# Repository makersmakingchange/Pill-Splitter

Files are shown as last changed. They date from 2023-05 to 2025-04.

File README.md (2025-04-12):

# Pill Splitter
The pill slicer is an easy to use device that slices a pill into two. This device is intended for users that need to cut pills into two and have difficulty doing so without crushing the pill.

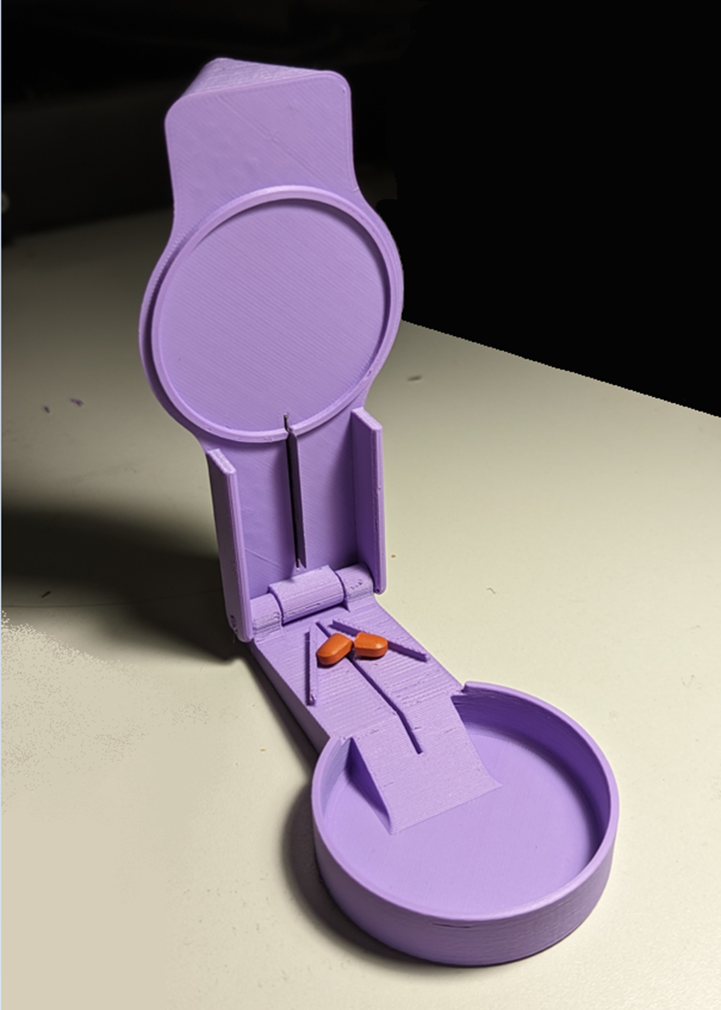
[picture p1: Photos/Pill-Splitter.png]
Picture of Pill Splitter.


## Makers Making Change Assistive Device Library
 - https://www.makersmakingchange.com/s/product/pill-splitter/01tJR00000092fJYAQ

## How to Obtain a Pill Splitter
### 1. Do it Yourself (DIY) or Do it Together (DIT)

This is an open-source assistive technology, so anyone is free to build it. All of the files and instructions required to build the Pill Splitter are contained within this repository. Refer to the Maker Checklist below.

### 2. Request a build of this device

If you would like to obtain a Pill Splitter, you may submit a build request through the [MMC Library Page](https://makersmakingchange.com/project/pill-splitter/). The requestor is responsible for the cost of materials and any shipping.

### 3. How to build this device for someone else

If you have the skills and equipment to build this device, and would like to donate your time to create the switch for someone who needs it, visit the [MMC Maker Wanted](https://makersmakingchange.com/maker-wanted/) section.

## Getting Started

### 1. Read the Makers Checklist

[The Makers Checklist](/Documentation/Pill_Splitter_Maker_Checklist_V1.0.pdf)

### 2. Order the Off-The-Shelf Components

The [Bill of Materials](/Documentation/Pill_Splitter_BOM_V1.0.xlsx) lists all of the parts and components required to build the Pill Splitter. The razor blades are also online or may be available in smaller quantities at your local dollar store.

### 3. Print the 3D Printable components

Print the components

All of the files and individual print files can be in the [/Build_Files/3D_Printing_Files](/Build_Files/3D_Printing_Files/) folder.

### 4. Assemble the Pill Splitter

Reference the [Assembly Guide](/Documentation/Pill_Splitter_Assembly_Guide_V1.0.pdf) for the tools and steps required to build each portion.

## Files
### Documentation
| Document             | Version | Link |
|----------------------|---------|------|
| Design Rationale     | 1.0     | [Pill_Splitter_Design_Rationale](/Documentation/Pill_Splitter_Design_Rationale_V1.0.pdf)     |
| Maker Checklist      | 1.0     | [Pill_Splitter_Maker_Checklist](/Documentation/Pill_Splitter_Maker_Checklist_V1.0.pdf)     |
| Bill of Materials    | 1.0     | [Pill_Splitter_Bill_of_Materials](/Documentation/Pill_Splitter_BOM_V1.0.xlsx)     |
| 3D Printing Guide    | 1.0     | [Pill_Splitter_3D_Printing_Guide](/Documentation/Pill_Splitter_3D_Printing_Guide_V1.0.pdf)     |
| Assembly Guide       | 1.0     | [Pill_Splitter_Assembly_Guide](/Documentation/Pill_Splitter_Assembly_Guide_V1.0.pdf)     |
| User Guide           | 1.0     | [Pill_Splitter_User_Guide](/Documentation/Pill_Splitter_User_Guide_V1.0.pdf)    |
| Changelog            | 1.0     | [Pill_Splitter_Changelog](/Documentation/Pill_Splitter_Changelog_V1.0.pdf)     |

### Design Files
 - [CAD Files](/Design_Files)

### Build Files
 - [3D Printing Files](/Build_Files/3D_Printing_Files)

## Attribution

Designers:
 - Initial design by [Aliaksei Petsiuk @apetsiuk - MyMiniFactory](https://www.myminifactory.com/users/apetsiuk)
 - Modifications and documentation by Neil Squire Society/Makers Making Change

## License
Everything needed or used to design, make, test, or prepare the Pill Splitter is licensed under the [Attribution-NonCommercial-ShareAlike 4.0 ](https://creativecommons.org/licenses/by-nc-sa/4.0/).

Accompanying material such as instruction manuals, videos, and other copyrightable works that are useful but not necessary to design, make, test, or prepare the Pill Splitter are published under a Creative Commons Attribution-ShareAlike 4.0 license https://creativecommons.org/licenses/by-sa/4.0/ (CC BY-SA 4.0).

---

<!-- ABOUT MMC START -->
## About Makers Making Change
[Makers Making Change Logo](https://www.makersmakingchange.com/)

Makers Making Change is a program of [Neil Squire](https://www.neilsquire.ca/), a Canadian non-profit that uses technology, knowledge, and passion to empower people with disabilities.

Makers Making Change leverages the capacity of community based Makers, Disability Professionals and Volunteers to develop and deliver affordable Open Source Assistive Technologies.

 - Website: [www.MakersMakingChange.com](https://www.makersmakingchange.com/)
 - GitHub: [makersmakingchange](https://github.com/makersmakingchange)
 - Bluesky: [@makersmakingchange.bsky.social](https://bsky.app/profile/makersmakingchange.bsky.social)
 - Instagram: [@makersmakingchange](https://www.instagram.com/makersmakingchange)
 - Facebook: [makersmakechange](https://www.facebook.com/makersmakechange)
 - LinkedIn: [Neil Squire Society](https://www.linkedin.com/company/neil-squire-society/)
 - Thingiverse: [makersmakingchange](https://www.thingiverse.com/makersmakingchange/about)
 - Printables: [MakersMakingChange](https://www.printables.com/@MakersMakingChange)

### Contact Us
For technical questions, to get involved, or to share your experience we encourage you to [visit our website](https://www.makersmakingchange.com/) or [contact us](https://www.makersmakingchange.com/s/contact).
<!-- ABOUT MMC END -->

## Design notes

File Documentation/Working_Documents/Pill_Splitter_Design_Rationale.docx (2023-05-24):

# Introduction

The pill slicer is an easy to use device that slices a pill into two. This device is intended for users that need to cut pills into two and have difficulty doing so without crushing the pill.

# Research

Name | Image | Price | Link

Commercial

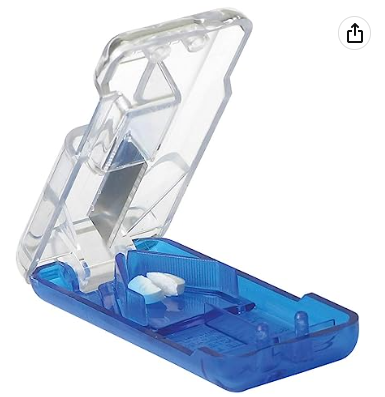
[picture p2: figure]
Image of the EZY DOSE Pill Cutter

EZY DOSE Pill Cutter | | 12.25 | Link (https://www.amazon.ca/Ezy-Dose-Pill-Cutter-Dispenser/dp/B001KYVO78?hvadid=459657913388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)

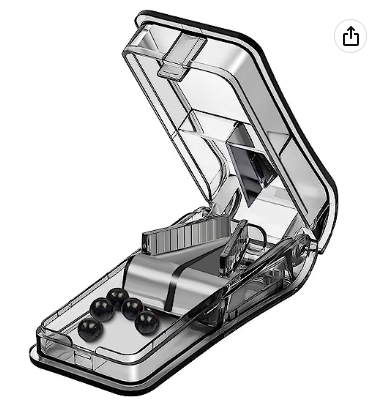
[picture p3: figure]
Image of the Pill Cutter

Pill Cutter | | 8.99 | Link (https://www.amazon.ca/Pill-Splitters-Portable-Vitamins-Medication/dp/B09TZSBPQC?s=hpc)

DIY

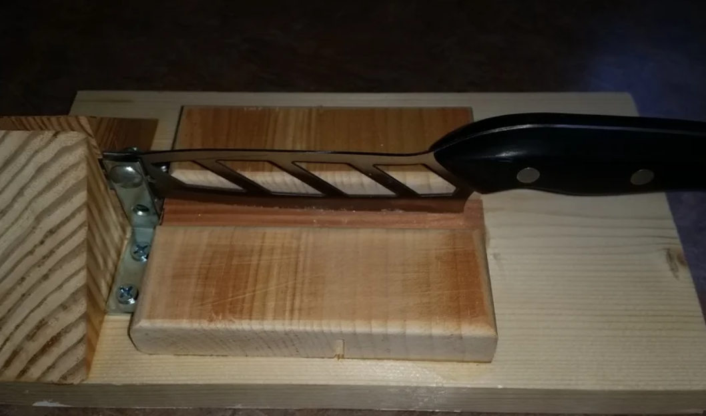
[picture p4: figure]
A knife bolted to a metal bracket on several pieces of wood.

DIY Multiple Pill Splitter | | N/A | Link (https://www.instructables.com/DIY-Multiple-Pill-Splitter/)

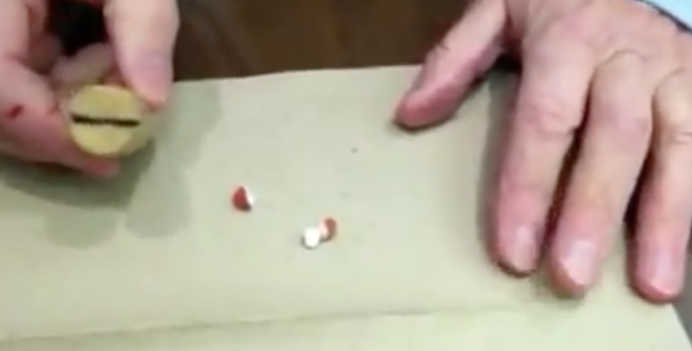
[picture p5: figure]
A crushed pill on a cutting board between two hands. One hand is holding a homemade pill splitter.

Homemade Pill Splitter | | N/A | Link (https://www.wpr.org/homemade-pill-splitter)

# Requirements

## Goals

G01 | Device must be able to easily slice a pill

## Functional Requirements

F01 | Device must use a replaceable slicing device
F02 | Device must be safe and difficult to injure yourself with.

## Constraints

C01 | Design must be entirely 3D printed

# Conceptual Design

Initial design was found on myminifactory.com by user Aliaksei Petsiuk @apetsiuk - MyMiniFactory (https://www.myminifactory.com/users/apetsiuk)

# Prototyping

After inspecting the files for the first version, it was found that there was no blade or method of slicing the pill mentioned in the original device posting. A version was designed that uses a standard disposable safety razor blade.

# Testing

After the first print of the updated design, it was found that the overhangs were too steep for most printers, leading to poor surface quality.

# Detailed Design

A final version was designed with better overhangs that are more printable and reduced print time by an hour.

# Opportunities for Improvement

More safety features could be added in addition to the blade fence to improve the safety of the device.

© 2023 by Neil Squire. This work is licensed under the CC BY SA 4.0 License: http://creativecommons.org/licenses/by-sa/4.0 Files available at https://makersmakingchange.com/project/pill-slicer/ Page 1 of 1

V1.0 | March 2023 Pill Slicer Design Rationale

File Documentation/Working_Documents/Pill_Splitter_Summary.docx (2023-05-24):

# Title

Pill Slicer

## Subtitle

The pill slicer is an easy to use device that slices a pill into two.

## Device Details

### Overview

This device is intended for users that need to cut pills into two and have difficulty doing so without crushing the pill.

### Usage

To use, place a pill over the slot on the lower base, and center it between the two fences. Close the upper half of the device, and the built in razor blade will slice the pill in half.

### Cost

<$5

### Build Instructions

After assembling the device as in the assemble guide, the razor blade can be flipped or replaced if the blade dulls and no longer cuts properly.

#### Skills Required

- 3D printing

#### Time Required

3D printing time: 394 min (6h34min)

Assembly Time: 5 min

#### Tools

- 3D printer
- Pliers
- Hobby knife
- Sandpaper

#### Components

#### 3D Printing

- Upper
- Lower
- Hinge Pin
- Blade Pin

### Attribution

Initial design by Aliaksei Petsiuk @apetsiuk - MyMiniFactory (https://www.myminifactory.com/users/apetsiuk)

Modifications and documentation by Neil Squire Society/Makers Making Change

© 2023 by Neil Squire. This work is licensed under the CC BY SA 4.0 License: http://creativecommons.org/licenses/by-sa/4.0 Files available at https://makersmakingchange.com/project/pill-slicer/ Page 1 of 1

V1.0 | March 2023 Pill Slicer Summary

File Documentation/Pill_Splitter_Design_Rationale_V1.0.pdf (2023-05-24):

V1.0 | March 2023

## Pill Slicer

## DESIGN RATIONALE

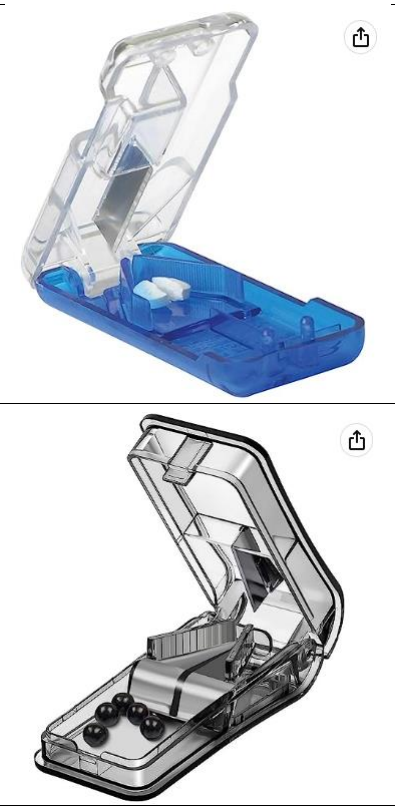
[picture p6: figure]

© 2023 by Neil Squire. (https://neilsquire.ca/)
This work is licensed under the CC BY SA 4.0 License: http://creativecommons.org/licenses/by-sa/4.0
Files available at https://makersmakingchange.com/project/pill-slicer/ | Page 1 of 3

### Introduction

The pill slicer is an easy to use device that slices a pill into two. This device is intended for users that need to cut pills into two and have difficulty doing so without crushing the pill.

### Research

Name | Image | Price | Link
Commercial
EZY DOSE Pill Cutter | 12.25 | Link (https://www.amazon.ca/Ezy-Dose-Pill-Cutter-Dispenser/dp/B001KYVO78?hvadid=459657913388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)
Pill Cutter | 8.99 | Link (https://www.amazon.ca/Pill-Splitters-Portable-Vitamins-Medication/dp/B09TZSBPQC?s=hpc)

DIY

## DESIGN RATIONALE

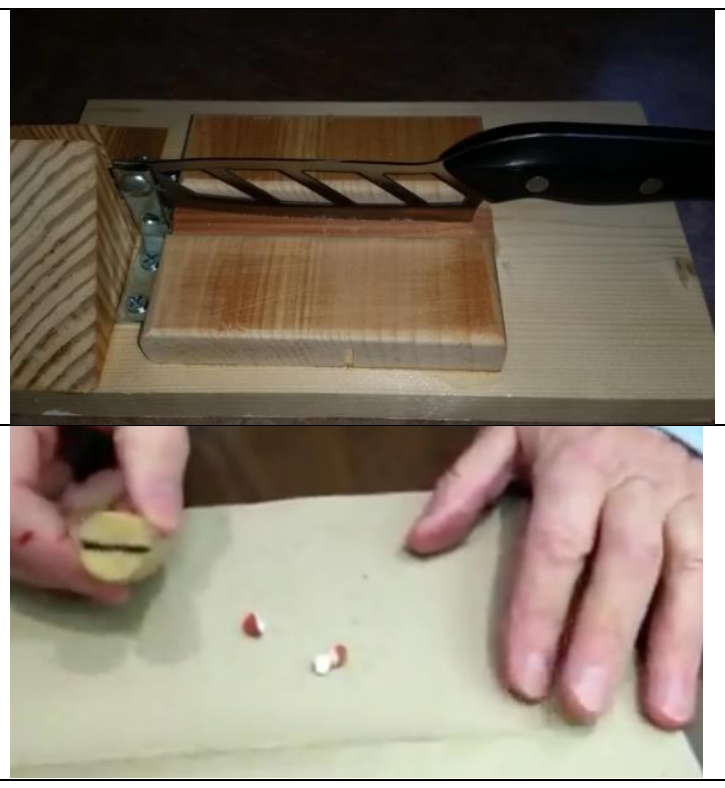
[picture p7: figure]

Files available at https://makersmakingchange.com/project/pill-slicer/ | Page 2 of 3
DIY Multiple Pill Splitter | N/A | Link (https://www.instructables.com/DIY-Multiple-Pill-Splitter/)
Homemade Pill Splitter | N/A | Link (https://www.wpr.org/homemade-pill-splitter)

### Requirements

### Goals

G01 Device must be able to easily slice a pill

### Functional Requirements

F01 | Device must use a replaceable slicing device
F02 | Device must be safe and difficult to injure yourself with.

### Constraints

C01 Design must be entirely 3D printed

### Conceptual Design

Initial design was found on myminifactory.com by user Aliaksei Petsiuk @apetsiuk - MyMiniFactory (https://www.myminifactory.com/users/apetsiuk)

### Prototyping

After inspecting the files for the first version, it was found that there was no blade or method of slicing the pill mentioned in the original device posting. A version was designed that uses a standard disposable safety razor blade.

## DESIGN RATIONALE

Files available at https://makersmakingchange.com/project/pill-slicer/ | Page 3 of 3

### Testing

After the first print of the updated design, it was found that the overhangs were too steep for most printers, leading to poor surface quality.

### Detailed Design

A final version was designed with better overhangs that are more printable and reduced print time by an hour.

### Opportunities for Improvement

More safety features could be added in addition to the blade fence to improve the safety of the device.

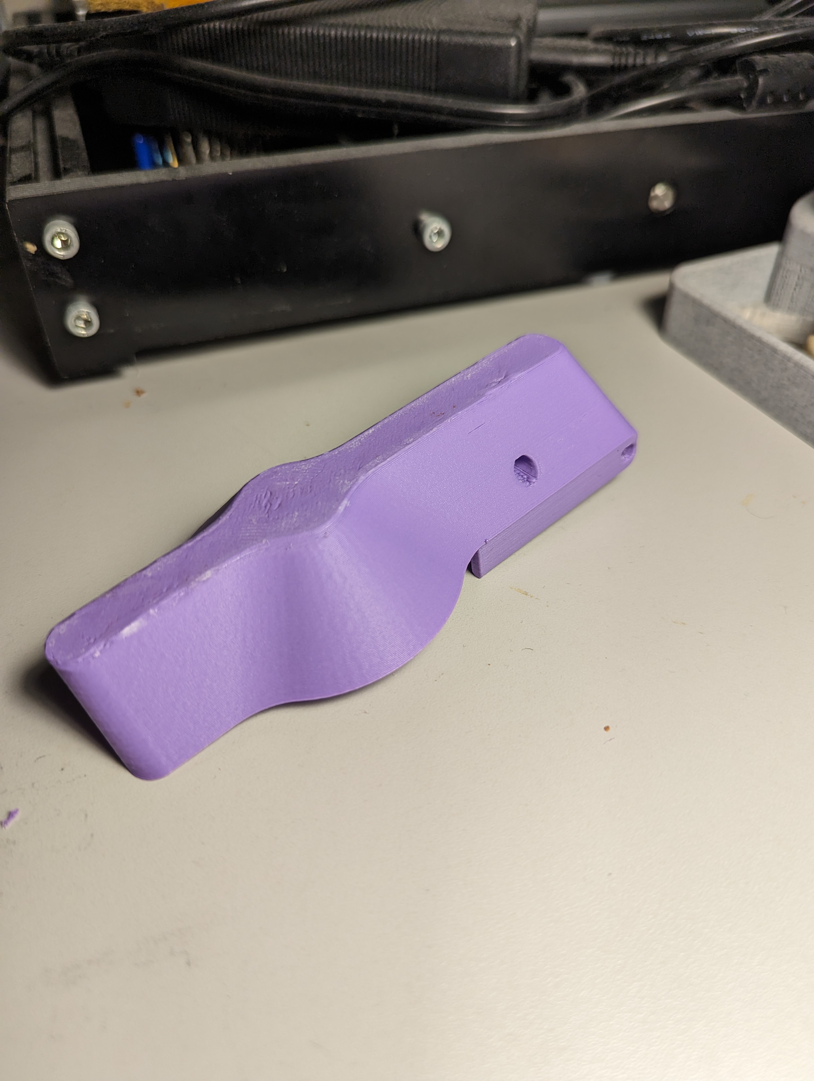
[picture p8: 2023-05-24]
Photos/upper-top.jpg

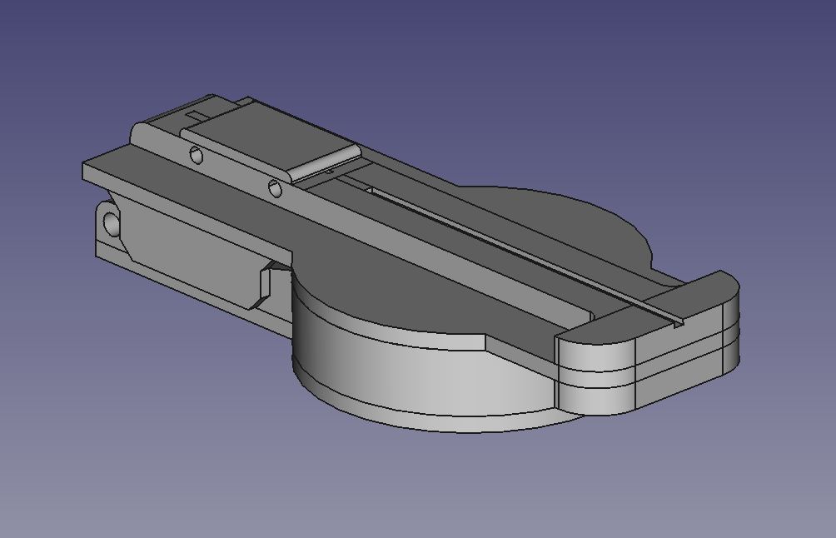
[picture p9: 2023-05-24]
Photos/capture.JPG

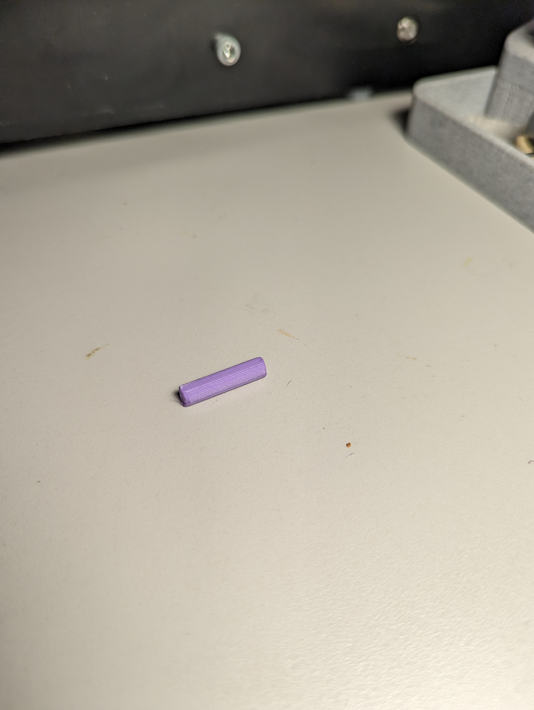
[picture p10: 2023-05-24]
Photos/blade pin.jpg

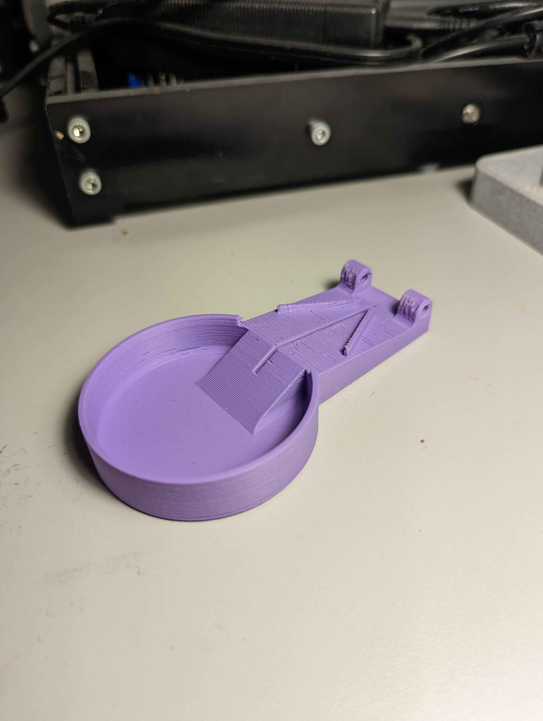
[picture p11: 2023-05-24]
Photos/lower.jpg

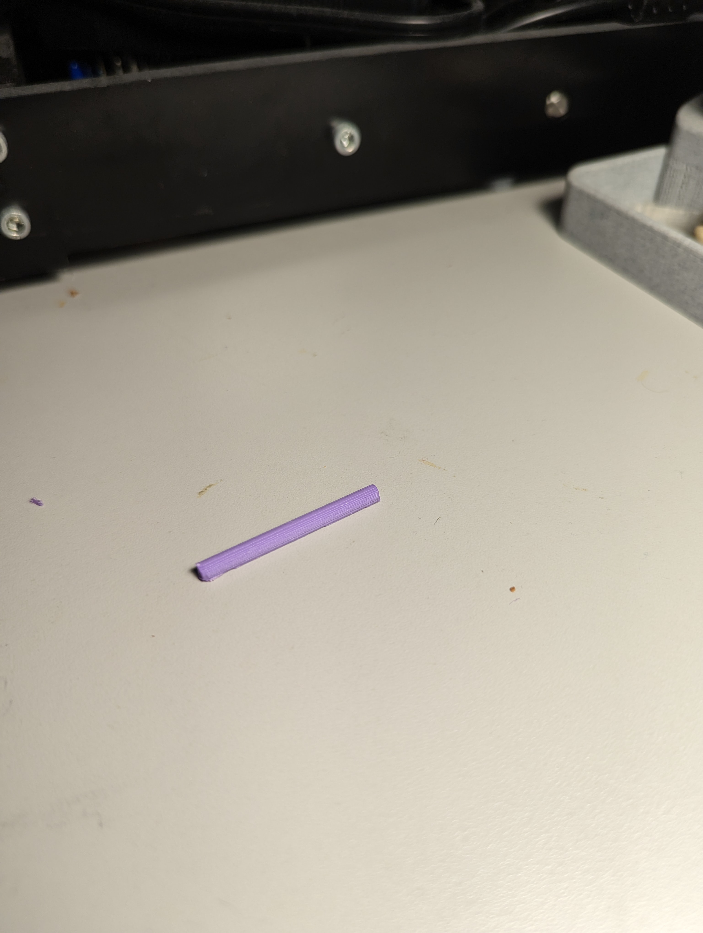
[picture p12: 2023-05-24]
Photos/hinge pin.jpg

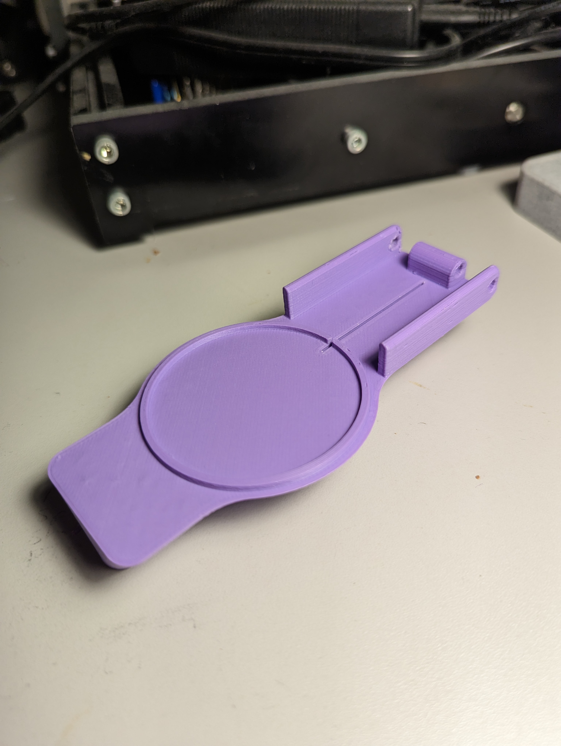
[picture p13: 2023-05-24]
Photos/upper-bottom.jpg

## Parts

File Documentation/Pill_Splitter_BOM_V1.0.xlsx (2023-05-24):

Device: Pill Slicer |  | Total Cost | Total Print time (hr) | Total filament (g)
Version: V1.0 | Date Created: 3/16/2023 | $2.06 | 6.57 | 53
Commercial Parts:
Part type (Electrical. Mechanical, Sanitization, ect) | Part Name | Quantity Needed | Pkg Quantity | Price per package | Price per Unit | Price for qty needed | Link
Mechanical | Razor Blade | 1 | 10 | $7.34 | $0.73 | $0.73 | https://www.amazon.ca/dp/B001G5FOLI?psc=1&ref=ppx_yo2ov_dt_b_product_details
 |  |  |  |  |  | $0.00
 |  |  |  |  |  | $0.00
3D Printed Parts ESTIMATED PRICING USING 1KG ROLL COST: | $25.00
Part | Description | Quantity Needed | TOTAL Mass (g) | Estimated Price | Print Time (Min) | Link
lower | lower body of the pill slicer | 1 | 20 | $0.50 | 163
upper | upper body of the pill slicer | 1 | 31 | $0.78 | 223
hinge pin | hinge pin | 1 | 1 | $0.03 | 4
blade pin | blade pin | 1 | 1 | $0.03 | 4
 |  |  |  | $0.00
 |  |  | Total Print Cost: | $1.32
Tools for Assembly
Pliers
Sandpaper
Hobby knife
Alternatives (if there are other sources for some parts link them below)
Part and description | Link

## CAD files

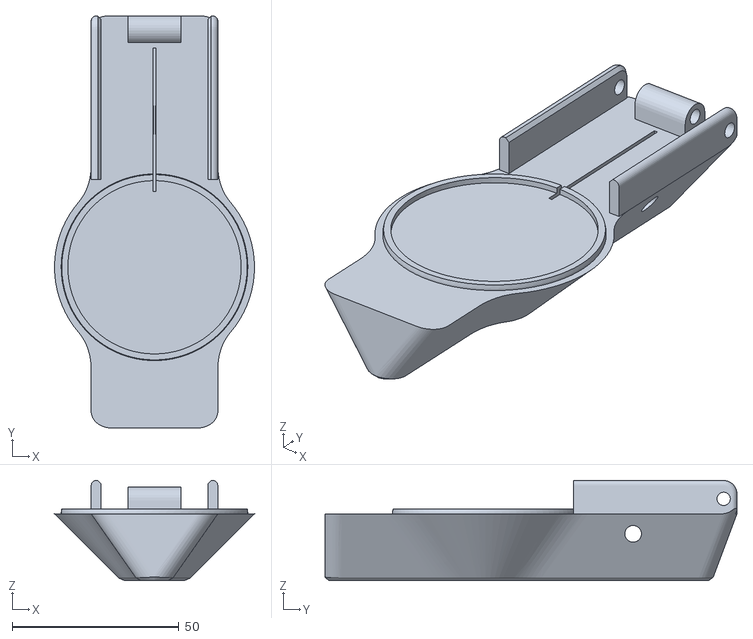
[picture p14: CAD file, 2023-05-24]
Build_Files/3D_Printing_Files/upper.stl
60.0 x 123.6 x 30.0

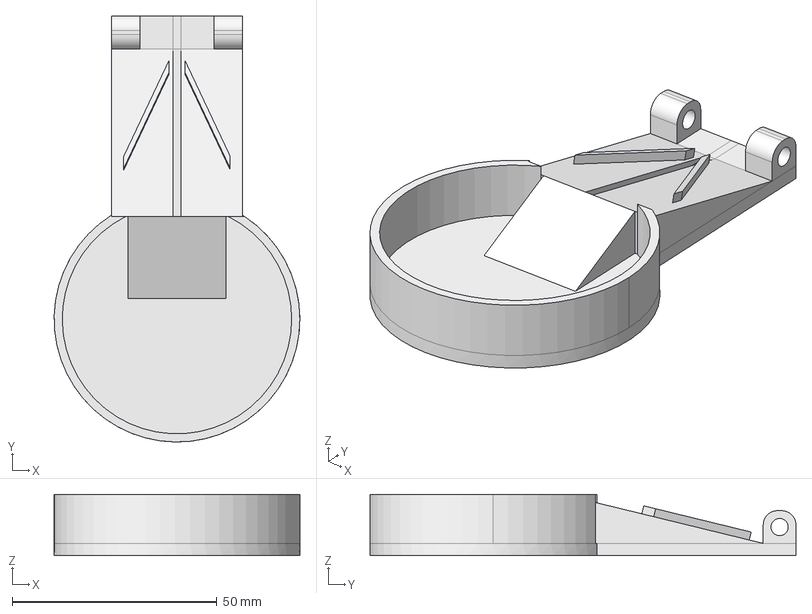
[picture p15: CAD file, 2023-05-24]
Design_Files/bottom-part.FCStd
60.0 x 104.0 x 15.0 mm

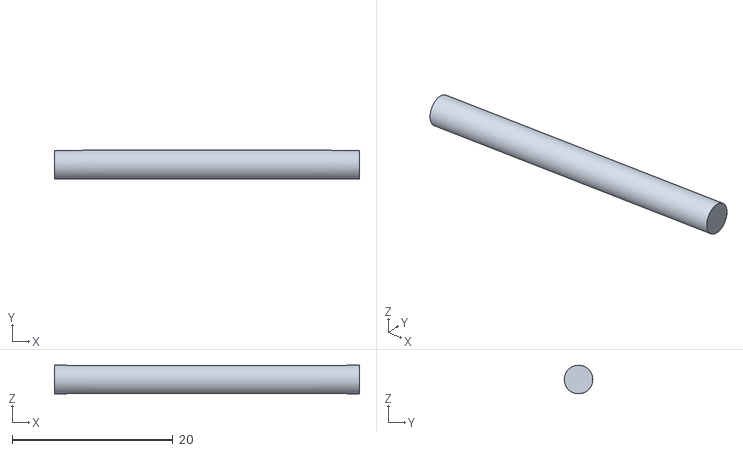
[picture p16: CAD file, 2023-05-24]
Build_Files/3D_Printing_Files/hinge_pin.stl
38.0 x 3.56 x 3.55

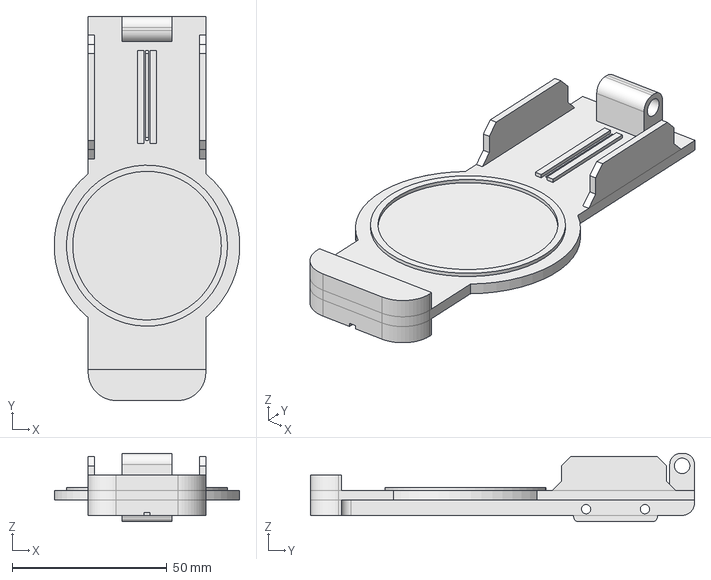
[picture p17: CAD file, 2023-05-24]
Design_Files/upper-part.FCStd
59.9 x 124.0 x 22.0 mm

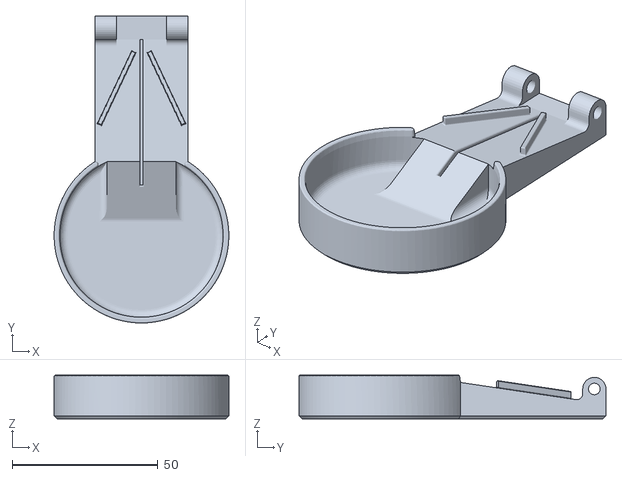
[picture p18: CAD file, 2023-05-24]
Build_Files/3D_Printing_Files/lower.stl
60.0 x 105.4 x 15.0

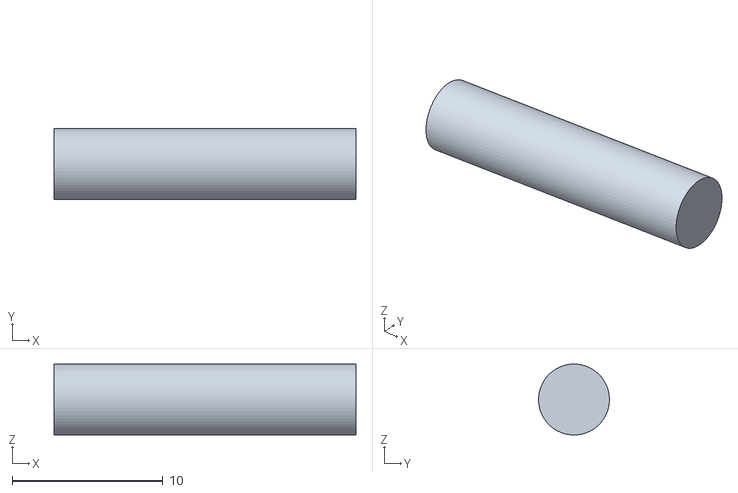
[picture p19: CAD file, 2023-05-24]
Build_Files/3D_Printing_Files/blade_pin.stl
20.0 x 4.70 x 4.70

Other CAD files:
Design_Files/Pill Slicer v6.f3z

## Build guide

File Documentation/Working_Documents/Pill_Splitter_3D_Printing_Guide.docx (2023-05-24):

# 3D Printing Summary

Metrics
Total Print Time (min) | 394
Total Number of Components | 4
Typical Total Mass (g) | 53
Typical Number of Print Setups | 4

# 3D Printing Settings

Print File Name | Qty | Total Print Time (hr:min) | Mass (g) | Infill (%) | Support(Y/N) | Layer Height/ Nozzle Diameter(mm) | Notes (orientation, special settings, etc.)
lower.stl | 1 | 2:43 | 20 | 20 | N | 0.2/0.4 | - Print in orientation given in STL
upper.stl | 1 | 3:43 | 31 | 20 | N | 0.2/0.4 | - Print in orientation given in STL
hinge_pin.stl | 1 | 0:04 | 0.5 | 20 | N | 0.2/0.4 | - Print in orientation given in STL
blade_pin.stl | 1 | 0.04 | 0.5 | 20 | N | 0.2/0.4 | - Print in orientation given in STL

# Customization Options

- The device can be printed in any colour the user would like.

# Post-Processing

- Remove all supports and remove any sharp edges with sandpaper and a hobby knife.

# Examples of Quality Prints

Photos of lower

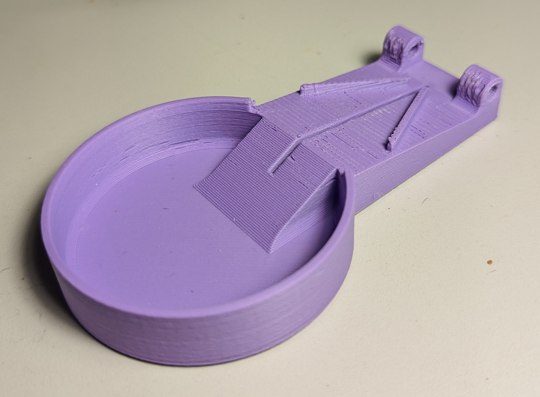
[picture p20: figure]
Good quality print of lower.stl

Photos of upper

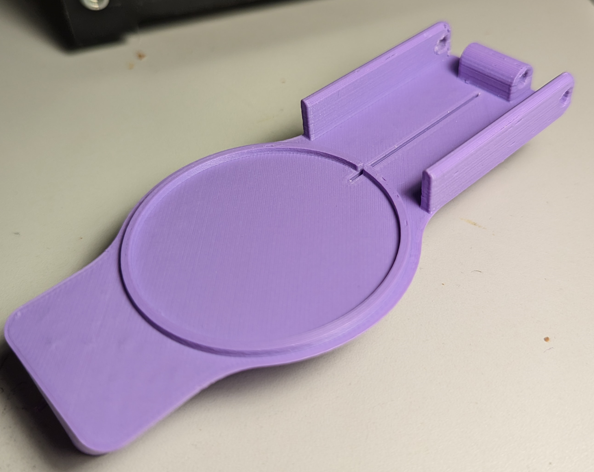
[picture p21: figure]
Bottom view of a good quality print of upper.stl
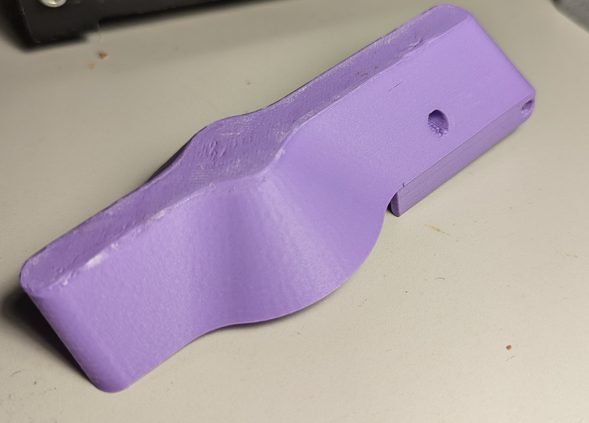
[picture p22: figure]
Top view of a good quality print of upper.stl

Photos of hinge pin

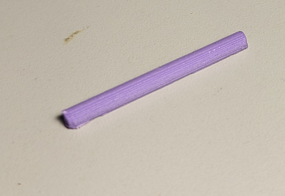
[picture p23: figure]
Good quality print of hinge_pin.stl

Photos of blade pin

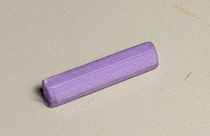
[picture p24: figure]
Good quality print of blade_pin.stl

© 2023 by Neil Squire. This work is licensed under the CC BY SA 4.0 License: http://creativecommons.org/licenses/by-sa/4.0 Files available at https://makersmakingchange.com/project/pill-slicer/ Page 1 of 2

V1.0 | March 2023 Pill Slicer 3D Printing Guide

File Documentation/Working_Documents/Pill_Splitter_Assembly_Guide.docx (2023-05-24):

# Required Components

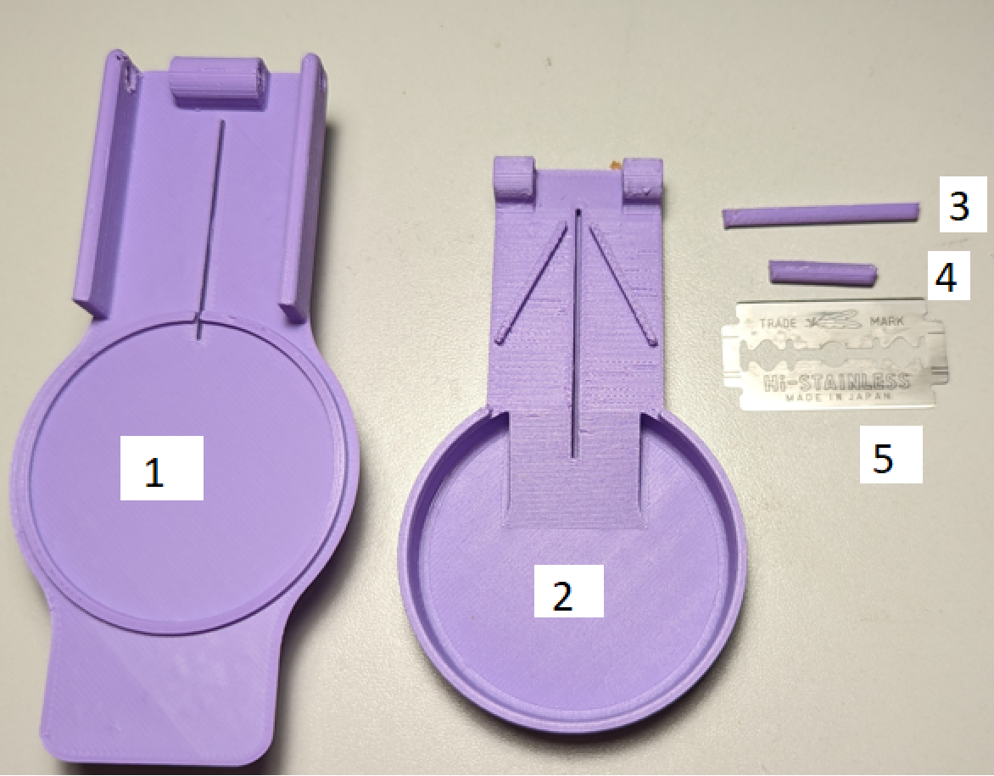
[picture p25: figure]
All the parts of the pill splitter on a pale background, numbered and ready for assembly

| BOM 1. Upper 2. Lower 3. Hinge Pin 4. Blade Pin 5. Razor Blade

# Required Tools

- Pliers
- Sandpaper
- Hobby knife

# Required Personal Protective Equipment (PPE)

- Safety Glasses

# Assembly Instructions

## Step 1

Using pliers, insert the razor blade into the slot in the upper piece of the slicer.

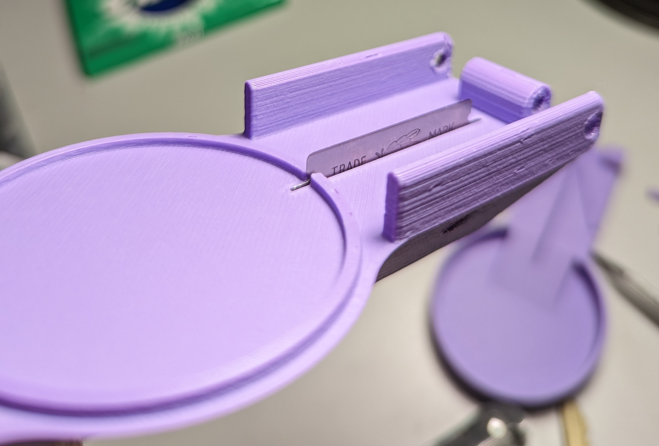
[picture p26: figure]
The upper portion of the pill slicer, with the razor blade inserted until just the blade is showing

## Step 2

Insert the blade pin to secure the blade in place. Make sure the pin is centred in the upper body.

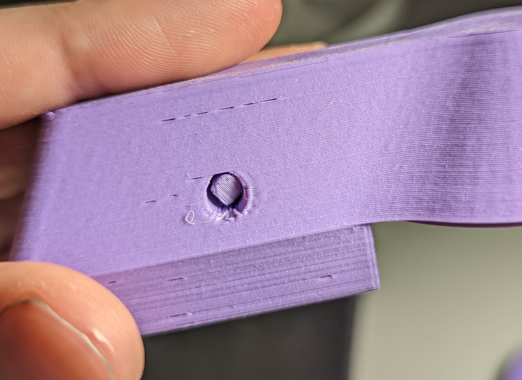
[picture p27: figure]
The upper half of the pill splitter, with the blade pin inserted through the hole in the body, securing the blade in place.

## Step 3

Place the upper body over the lower body, and align the hinge pins.

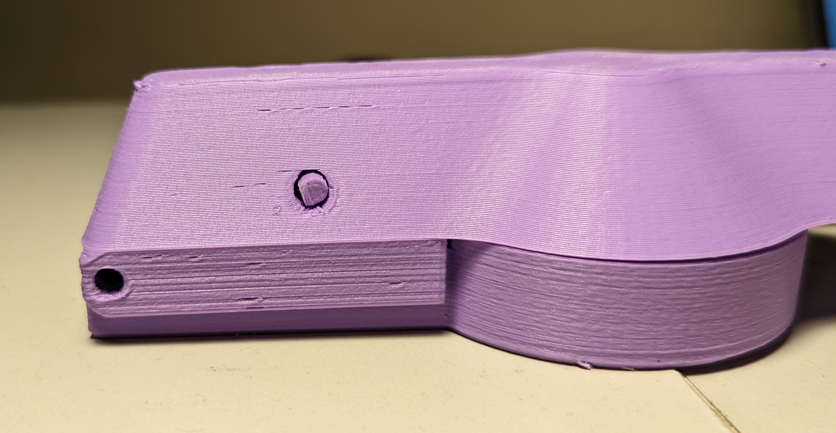
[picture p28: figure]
The upper portion of the assembly placed over the lower portion, with the hinge holes aligned.

## Step 4

Insert the hinge pin, and centre it in the holes.

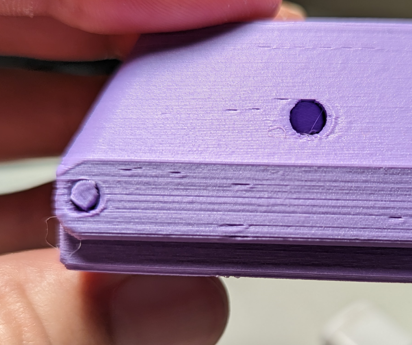
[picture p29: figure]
The hinge pin inserted through the hinge holes in the previous assembly.

© 2023 by Neil Squire. This work is licensed under the CC BY SA 4.0 License: http://creativecommons.org/licenses/by-sa/4.0 Files available at https://makersmakingchange.com/project/pill-slicer/ Page 1 of 1

V1.0 | March 2023 Pill Slicer Assembly Guide

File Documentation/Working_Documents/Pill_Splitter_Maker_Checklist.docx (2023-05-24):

# Maker To Do List

- Read through the Assembly Guide to become familiar with required components, tools, supplies, and safety gear and overall assembly steps.
- Talk to User about customization options (e.g., color, any special requests, etc.)
- Order hardware components
- Gather tools, supplies, and safety equipment.
- Assemble the device
- Test device
- Print “User Quick Guide”

# Items to Give to User

- Assembled, tested device
- “User Quick Guide”

© 2023 by Neil Squire. This work is licensed under the CC BY SA 4.0 License: http://creativecommons.org/licenses/by-sa/4.0 Files available at https://makersmakingchange.com/project/pill-slicer/ Page 1 of 1

V1.0 | March 2023 Pill Slicer Maker Checklist

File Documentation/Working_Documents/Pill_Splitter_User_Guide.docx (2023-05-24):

## Introduction

The pill slicer is an easy to use device that slices a pill into two. This device is intended for users that need to cut pills into two and have difficulty doing so without crushing the pill.

## Features

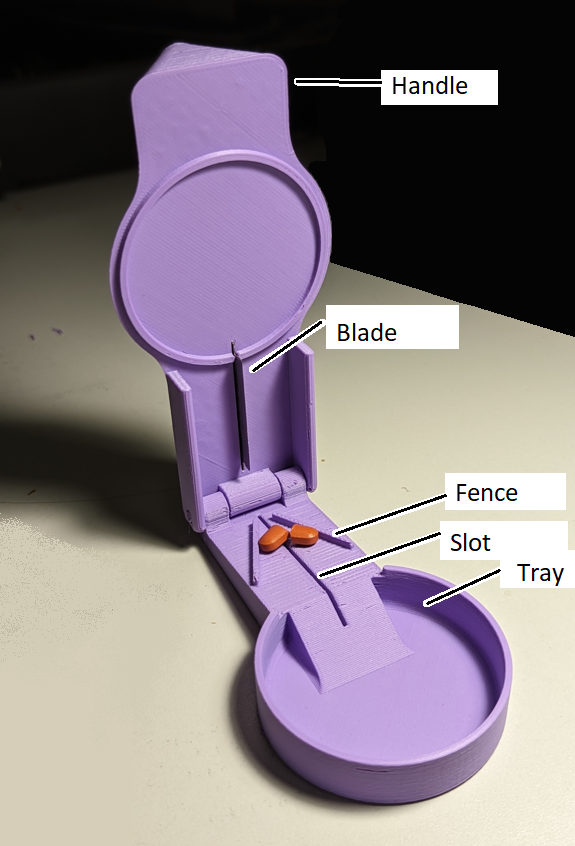
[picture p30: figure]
The purple pill splitter on a dark background with all the features labeled. There is a ibuprofen on the device that has already been cut in half.

## Usage

To use, place a pill over the slot on the lower base, and center it between the two fences. Close the upper half of the device, and the built in razor blade will slice the pill in half.

## Compatibility

This device is compatible with compressed, solid type pills. Liquid or powder pills that would spill if cut in half are not ideal for this type of device.

## Specifications

Length: 125mm

Width: 60mm

Height: 35mm

Weight: 50g

## Cleaning

Device can be wiped down with a damp cloth.

© 2023 by Neil Squire. This work is licensed under the CC BY SA 4.0 License: http://creativecommons.org/licenses/by-sa/4.0 Files available at https://makersmakingchange.com/project/pill-slicer/ Page 2 of 3

V1.0 | March 2023 Pill Slicer user Quick Guide

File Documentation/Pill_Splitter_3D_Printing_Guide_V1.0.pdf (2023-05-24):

V1.0 | March 2023

## Pill Slicer

## 3D PRINTING GUIDE

© 2023 by Neil Squire. (https://neilsquire.ca/)
This work is licensed under the CC BY SA 4.0 License: http://creativecommons.org/licenses/by-sa/4.0
Files available at https://makersmakingchange.com/project/pill-slicer/ | Page 1 of 3

### 3D Printing Summary

Metrics
Total Print Time (min) | 394
Total Number of Components | 4
Typical Total Mass (g) | 53
Typical Number of Print Setups | 4

### 3D Printing Settings

Print File Name | Qty | Total Print Time (hr:min) | Mass (g) | Infill (%) | Support(Y/N) | Layer Height/ Nozzle Diameter(mm) | Notes (orientation, special settings, etc.)
lower.stl | 1 | 2:43 | 20 | 20 | N | 0.2/0.4 | -Print in orientation given in STL
upper.stl | 1 | 3:43 | 31 | 20 | N | 0.2/0.4 | -Print in orientation given in STL
hinge_pin.stl | 1 | 0:04 | 0.5 | 20 | N | 0.2/0.4 | -Print in orientation given in STL
blade_pin.stl | 1 | 0.04 | 0.5 | 20 | N | 0.2/0.4 | -Print in orientation given in STL

### Customization Options

- The device can be printed in any colour the user would like.

### Post-Processing

- Remove all supports and remove any sharp edges with sandpaper and a hobby knife.

## 3D PRINTING GUIDE

### Examples of Quality Prints

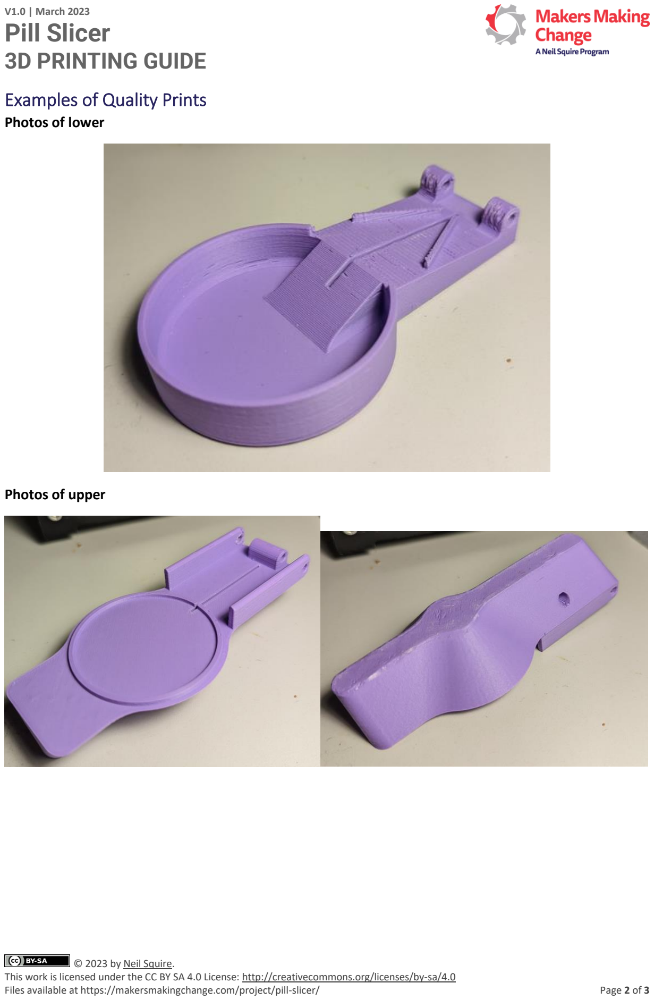
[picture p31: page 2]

Files available at https://makersmakingchange.com/project/pill-slicer/ | Page 2 of 3

Photos of lower

Photos of upper

## 3D PRINTING GUIDE

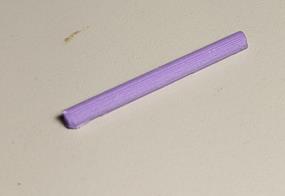
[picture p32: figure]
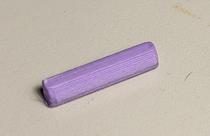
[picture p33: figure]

Files available at https://makersmakingchange.com/project/pill-slicer/ | Page 3 of 3

Photos of hinge pin

Photos of blade pin

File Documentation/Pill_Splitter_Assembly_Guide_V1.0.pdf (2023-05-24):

V1.0 | March 2023

# Pill Slicer

# ASSEMBLY GUIDE

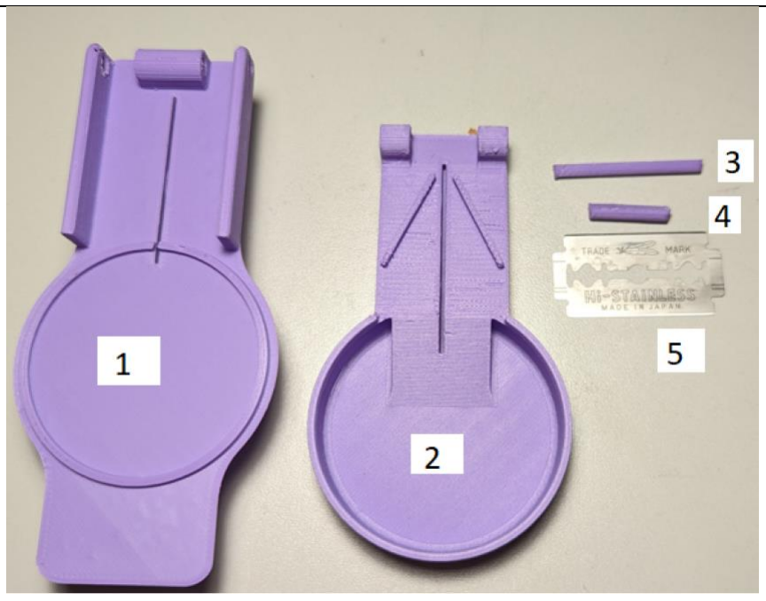
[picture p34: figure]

© 2023 by Neil Squire. (https://neilsquire.ca/)
This work is licensed under the CC BY SA 4.0 License: http://creativecommons.org/licenses/by-sa/4.0
Files available at https://makersmakingchange.com/project/pill-slicer/ | Page 1 of 3

# Required Components

## BOM 1. Upper 2. Lower 3. Hinge Pin 4. Blade Pin 5. Razor Blade

# Required Tools

## - Pliers - Sandpaper - Hobby knife

# Required Personal Protective Equipment (PPE)

## - Safety Glasses

# ASSEMBLY GUIDE

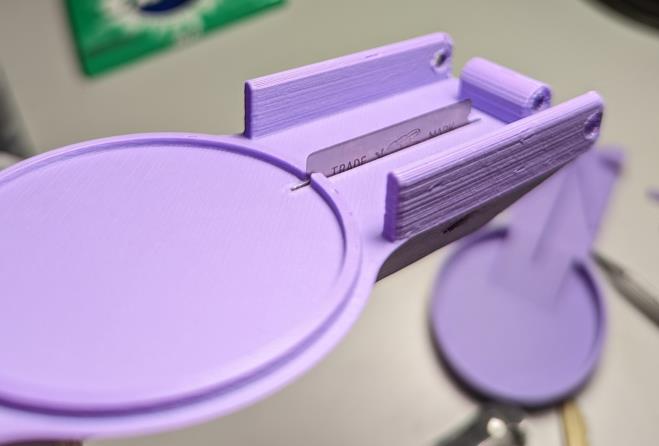
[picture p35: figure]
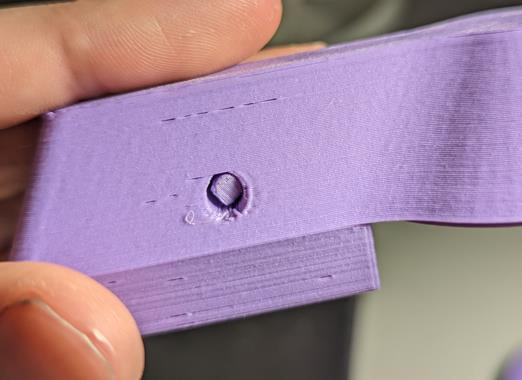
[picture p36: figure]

Files available at https://makersmakingchange.com/project/pill-slicer/ | Page 2 of 3

# Assembly Instructions

## Step 1

Using pliers, insert the razor blade into the slot in the upper piece of the slicer.

## Step 2

Insert the blade pin to secure the blade in place. Make sure the pin is centred in the upper body.

# ASSEMBLY GUIDE

## Step 3

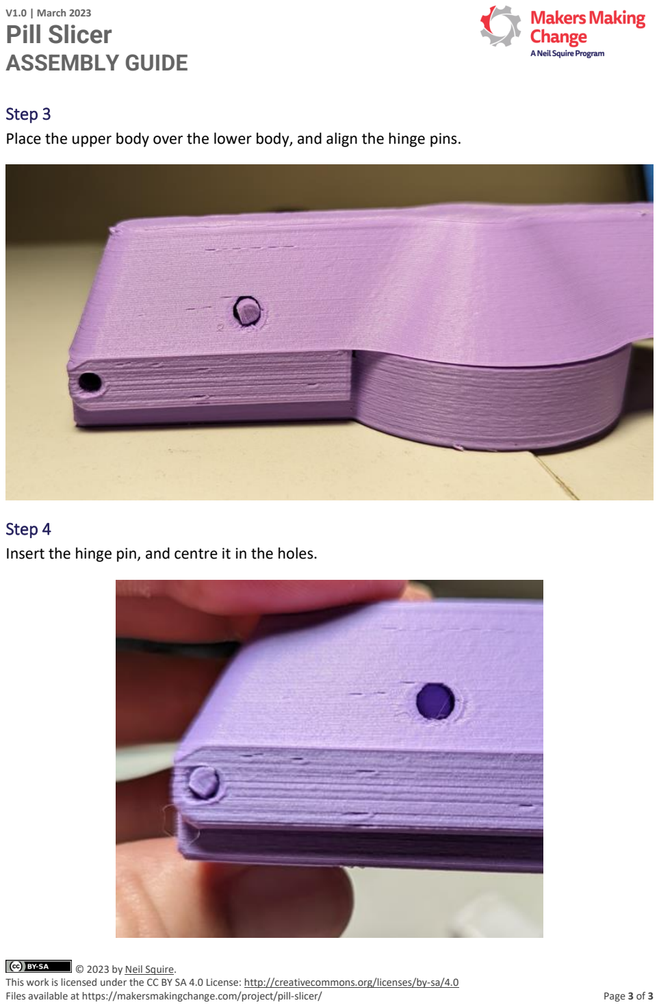
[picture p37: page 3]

Files available at https://makersmakingchange.com/project/pill-slicer/ | Page 3 of 3

Place the upper body over the lower body, and align the hinge pins.

## Step 4

Insert the hinge pin, and centre it in the holes.
